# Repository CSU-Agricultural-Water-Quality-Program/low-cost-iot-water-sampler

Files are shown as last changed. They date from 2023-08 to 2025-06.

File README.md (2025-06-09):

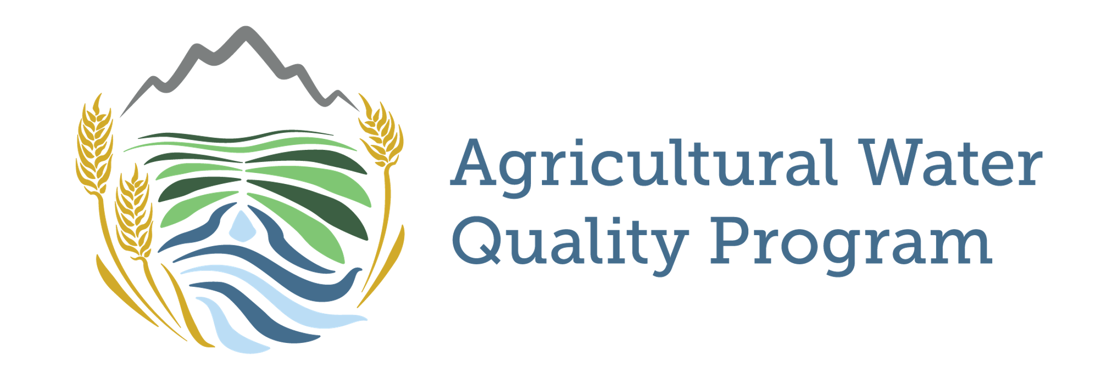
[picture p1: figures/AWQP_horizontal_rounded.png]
AWQP Logo (https://waterquality.colostate.edu)




# AWQP Low-Cost IoT Water Sampler
A low-cost, automated water sampler (LCS) with Internet of Things (IoT) technology for scalable, near-real-time water quality research developed by the Colorado State University Agricultural Water Quality Program (AWQP).

> [!NOTE]
> This project is actively under development. Code, parts, instructions, and other content are subject to change as we enhance the LCS. If you download/clone/fork this repository, we ask that you **please [email us directly](mailto:ansley.brown@colostate.edu;e.deleon@colostate.edu;erik.wardle@colostate.edu?subject=Inquiry%20about%20the%20Low%20Cost%20IoT%20Water%20Sampler%20from%20GitHub)** for the most up-to-date information and resources. We will also email you with any news related to the project moving forward!

## Table of Contents
- [Why create a low-cost water sampler?](#why-create-a-low-cost-water-sampler?)
- [Repo Contents](folder-contents)
- [Low Cost Sampler Description](#low-cost-sampler-description)
- [3D prints](#3D-prints)
- [Parts List](#parts-list)
- [How-to guide](#how-to-guide)
- [Known Bugs](#known-bugs)
- [Future Developments](#future-developments)
- [How to Cite](#how-to-cite)
- [License](#license)

---

## Why create a low-cost water sampler?
In Colorado and across the United States, agriculture is being identified as one source of nutrient
pollution in State and Federal waters. Nutrients such as nitrogen and phosphorus run off
farmlands and accumulate in surface waterways, causing water quality issues. Although
agricultural nonpoint sources are not currently regulated in Colorado, initiatives are set up to
encourage the adoption of Best Management Practices (BMPs) that protect surface water quality.
Quantifying BMP impacts on water quality, requires robust, edge-of-field (EoF) monitoring
systems that can accurately measure flow and collect water for nutrient and sediment analysis.
NRCS EoF standards currently require equipment that is often too costly for pragmatic and
scalable research. To address this need, the [Colorado State University Agricultural Water Quality
Program (AWQP)](https://waterquality.colostate.edu) has developed a low-cost, automated water sampler (LCS) with Internet of
Things (IoT) technology for scalable, near-real-time water quality research. This work directly
follows deliverables from an awarded NRCS Conservation Innovation Grant titled, “Next
Generation Technology for Monitoring Edge-of-Field Water Quality in Organic Agriculture”. The
CSU AWQP intends to create additional research and regulation opportunities for Colorado and beyond using this technology.

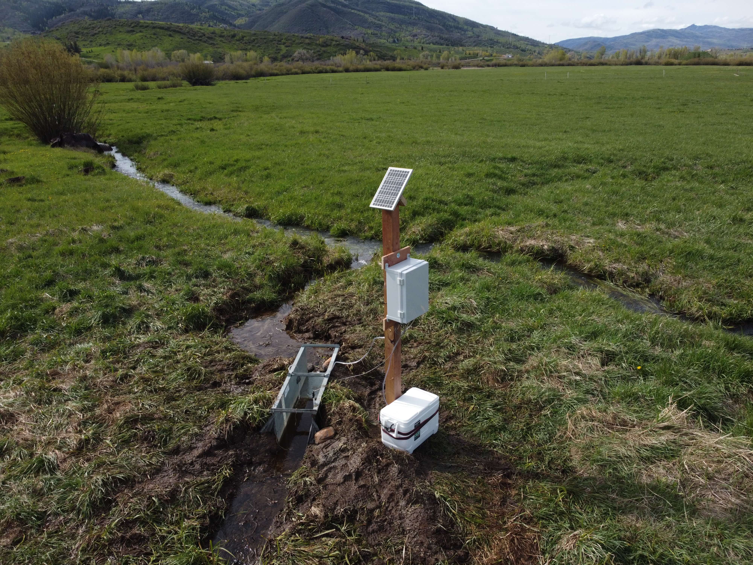
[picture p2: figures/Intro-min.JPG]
a deployed water sampler

**Figure 1.** Image of the low-cost automated water sampler (LCS) deployed at a mountain meadow hay field near Steamboat Springs, Colorado.

To learn more about AWQP, please visit [the AWQP website](https://waterquality.colostate.edu).

## Repo Contents
- .vscode
    - settings for flashing in VS code using the particle workbench add-on.
- compiled-firmwares
    - previously compiled firmwares for various borons (current code requires a unique binary for each device to accomodate for individual e-tape calibration)
- figures
    - figures embedded into README.md
- files
    - 3D prints: contains .STL files for printing that required for assembly
    - Bill of Materials: Excel with BOM, links, and prices 
- lib
    - libraries used in source code
- src
    - source code for particle boron flashing
    - config.h template for storing sensitive information like API keys and device-specific information needed to operate the LCS
- target
    - available firmware targets for particle devices
- .gitignore
    - files and folders to ignore when committing to the repository (e.g., config.h)
- AUTHORS.md
    - list of authors and contributors to the project
- CITATION.cff
    - citation file for the project, please use this to cite the LCS in your work
- CODE_OF_CONDUCT.md
    - code of conduct for the project, please read before contributing
- CONTRIBUTING.md
    - guidelines for contributing to the project, please read before contributing
- LICENSE.md
    - licensed under GNU General Public License Version 2 (GNU GPL V2.0)
- project.properties
    - contains project code and library dependencies
    
## Low Cost Sampler Description
The AWQP-developed LCS is comprised of five main components as shown in Figure 2: 1) device control panel 2) power assembly 3) pump assembly 4) a water depth sensor (eTape, MileOne), and 5) the water storage apparatus. 

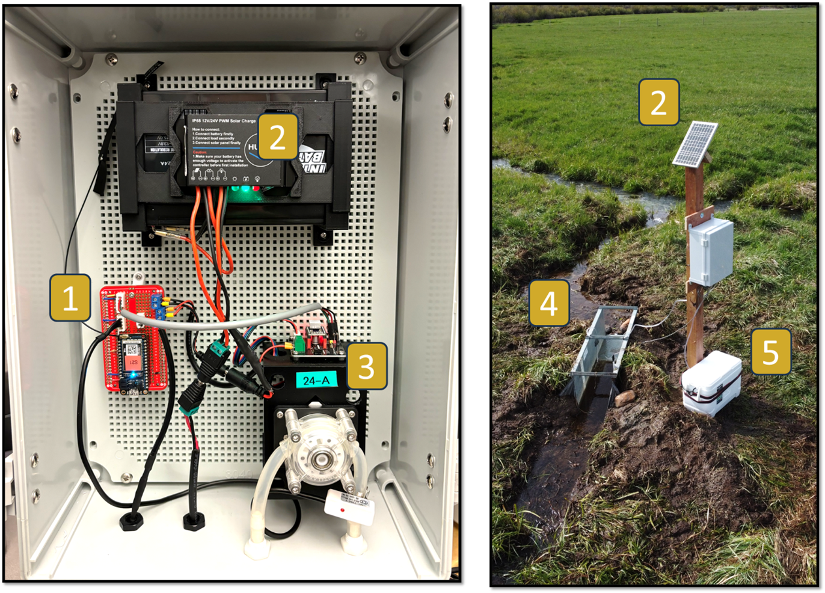
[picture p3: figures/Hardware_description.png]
low-cost sampler image

**Figure 2.** Picture of the low-cost automated water sampler (LCS) deployed in-situ, with its primary components annotated

Like commercial models, the LCS can detect and measure water flow in an installed flume via
depth, sample water at pre-determined or user-triggered intervals (in this case, hourly), preserve
water samples for later collection, remote data monitoring through cellular communications, and
stay powered remotely through solar and battery means. However, the LCS model accomplishes
this at approximately 1/10th of the cost of a commercial apparatus ($700-1,000). Additionally,
commercial models require the additional purchase of a cellular modem for wireless
connectivity, whereas the LCS integrally incorporates it into the microcontroller itself. Upon
completion of this experiment, the AWQP intends to open-source the LCS for future
collaborative development and sharing via GitHub repository on the AWQP GitHub
organization.

A preliminary comparison study performed by the AWQP indicate strong agreement between
LCS depth measurements and commercial bubbler units, with a root mean squared error (RMSE)
of 4.2 mm (n=1099). Additionally, measured analyte concentrations (total suspended solids,
NO3, NO2, Total N, Orthophosphate, Total Phosphorous) were similar, but lacked enough
sample points to accurately make a comparison. An example runoff depth measurement
comparison from an irrigation event at a corn field in Fort Collins, CO in 2020 is shown in
Figure 2.

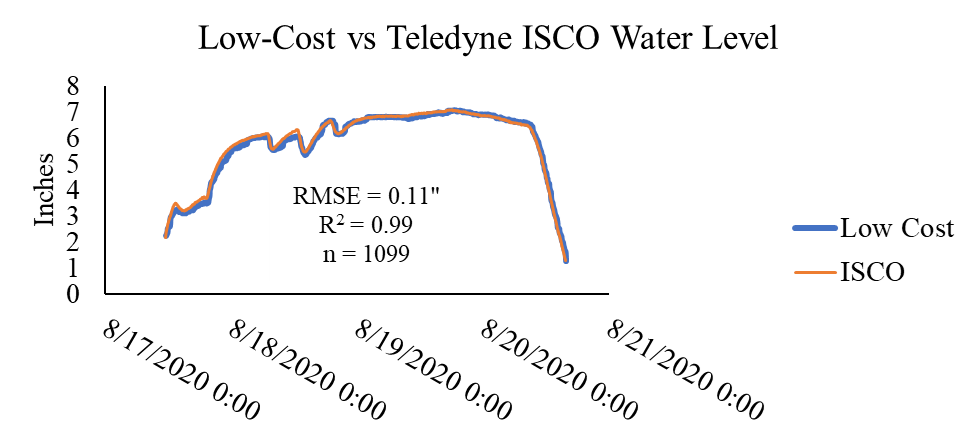
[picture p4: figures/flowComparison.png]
flow comparison graph

**Figure 3.** Results from a preliminary flow comparison study between the LCS and commercial Teledyne ISCO 6712 automated sampler.

## Software
- Particle Account and Particle Workbench on Virtual Studio Code is needed to claim a Particle Boron and flash calibration and sampler code.  
- Blynk IoT controls and monitors the LCS remotely via phone app. 
- (optional) Ubidots offers storage and visualization of sampler data. 

## 3D-prints
Can be found on our [AWQP Printables page](https://printables.com/@AgWaterQuality_66019):
* [Peristaltic pump mount](https://printables.com/model/560168-mount-for-a-peristaltic-pump)
* [12v Battery  mount](https://printables.com/model/560141-awqp-12v-battery-mount-for-the-low-cost-sampler)
* [Solar Controller Mount](https://www.printables.com/model/1177165-solar-controller-huine-mount-for-low-cost-iot-wate)
* [eTape TPU Cover](https://www.printables.com/model/1177200-milone-etape-tpu-protective-cover-for-awpq-low-cos) 

## Bill of Materials 
Please [contact the AWQP](mailto:ansley.brown@colostate.edu;e.deleon@colostate.edu;erik.wardle@colostate.edu?subject=Inquiry%20about%20the%20Low%20Cost%20IoT%20Water%20Sampler%20from%20GitHub) for the most current part list; these are often changing and being updated as improvements get implemented!

Current list updated 03 Jun. 2025:

[Bill of Materials](files/Bill%20of%20Materials.xlsx) 

## How-to guide
Introduction to major hardware components with a brief description:

- Enclosure: Protects the sampler components from the environment
- Pump Assembly: a peristaltic pump to collect water samples 
    - DRV8825 Motor Driver: Controls peristaltic pump with precision and efficiency
    - Non-contact water sensor: Detects water priming the pump
- Power Assembly: 12-volt Battery 
    - Solar Panel (10W): Charges Battery 
    - Solar Charging/Controller: Regulates power from the solar panel to the battery 
- Device Control Unit: PCB Carrier for the Particle Boron Microprocessor and all sensor connection points
- Water Depth Sensor: Using a eTape Water Level Sensor to monitor water level in flumes or streams. 
    - **Note:** For outdoors used  the sturdy eTape cable directly from the manufacturer, Milone Technologies.
- Water Storage Apparatus: Holds sample bottles and keeps collected samples cool. 

Brief Overview: 

1. Purchase all necessary hardware components (see [Bill of Materials](/files/Bill%20of%20Materials.xlsx))
2. 3D-print necessary mounting parts
3. Assemble hardware - [Here's our video guide!](https://youtu.be/WXuII_zaUJU?si=he2FRvl1eTsFYpLh)

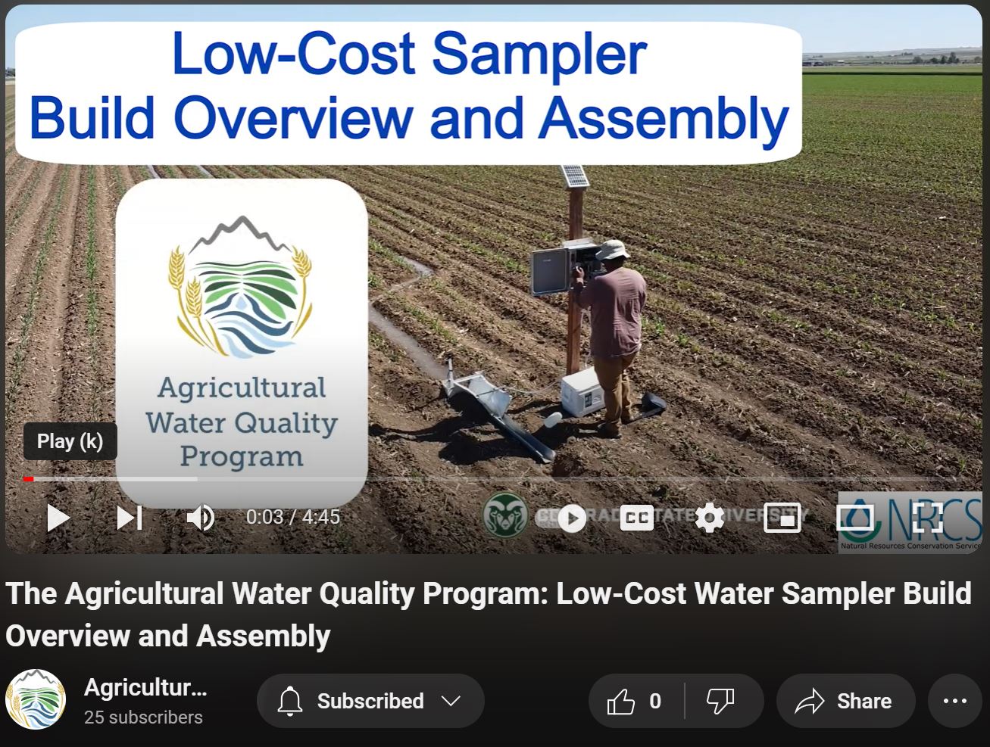
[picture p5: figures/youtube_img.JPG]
low cost sampler installation video (https://youtu.be/WXuII_zaUJU?si=he2FRvl1eTsFYpLh)


<br>  **Device Control Panel:** 

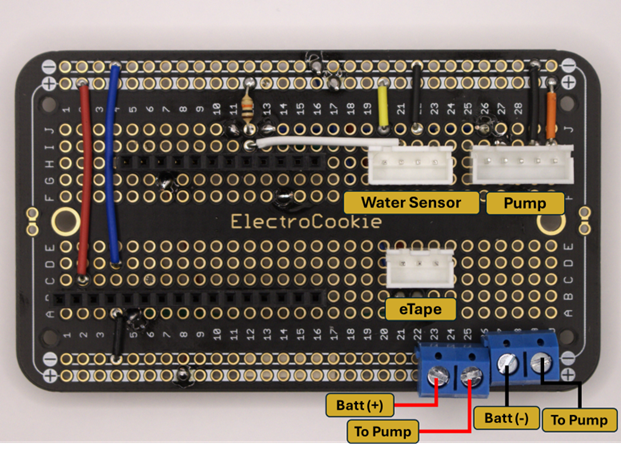
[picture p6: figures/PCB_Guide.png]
PCB Guide

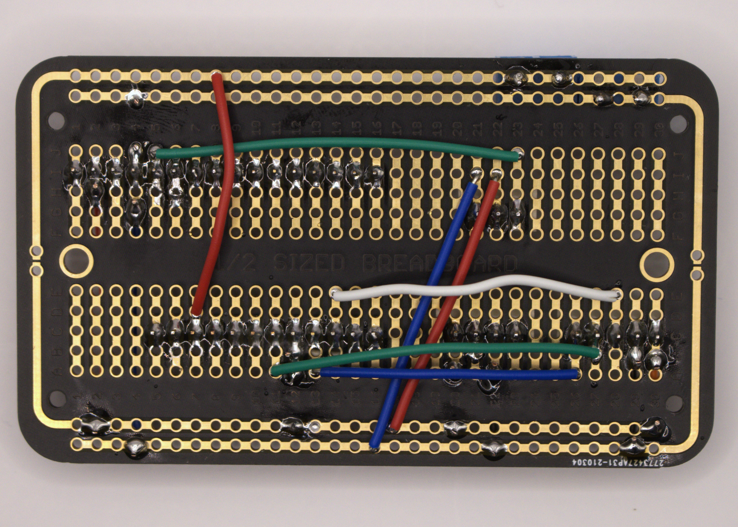
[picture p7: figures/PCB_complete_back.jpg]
    

**Figure 4.** Device Control Panel:  PCB front and back with wiring connection layouts and labels 

<br>

4. Make Blynk account and install Blynk phone application - [Bynk application website](https://blynk.io/)

The LCS requires user inputs to program the sampling protocol. These inputs include Volume to Sample (mL), Sampling Interval (min), Threshold (cm), Sample Bottle (mL). Using Blynk, users will input how much volume to collect (max 700mL per sample interval), how often to sample in minutes, the threshold depth in centimeters that will activate your sampler to start collecting water, and how large is the sample bottle to prevent sample slipovers.

- Setup Template 
- Add the following Datastreams as virtual pins 

<br>

| Name              | Virtual Pin | Data Type | Unit   | Min-Max    | Default |
|:-----------------:|:-------------:|:-----------:|:--------:|:------------:|:---------:|
| mL to Sample      | V1          | Integer   | (mL)   | 0 - 700   | 200     |
| Terminal Status   | V2          | String    |        |            |         |
| Sample Interval   | V3          | Integer   | (min)  | 0 - 720    | 60      |
| Threshold         | V4          | Integer   | (cm)   | 0 - 100    | 100     |
| Sample Bottle     | V5          | Integer   | (mL)   | 0 - 10000  | 2000    |
| Sample Now        | V9          | Integer   |        |            |         |
| mL to Collect     | V12         | Integer   | (mL)   | 0 - 1000   | na      |
| Current Threshold | V14         | Integer   | (cm)   | 0 - 100    | na      |
| Current Depth     | V17         | Integer   | (cm)   | 0 - 100    | na      |

<br>

5. (optional) Make Ubidots account - [Ubidots website](https://industrial.ubidots.com/)
6. eTape and Pump Calibration

    - eTape Calibration [Repo](https://github.com/CSU-Agricultural-Water-Quality-Program/AWQP-LCS-Etape-Calibration/tree/main) 
    - Pump Calibrtion [Repo](https://github.com/CSU-Agricultural-Water-Quality-Program/AWQP_LCS_pump_calibration)

7. Flash code from this repo, after updating the `config.h` file with your TOKENs from Blynk and Ubidots
8. Use the Blynk app to program your sampler 
9. Deploy and Enjoy!

### Configuration file instructions

For the code to run properly, you'll need to set up a `config.h` file with your API keys and other configurations.

1. **Navigate to the `src` directory**:
   - Inside the `src` directory, you will find a template file named `config_template.h`.

2. **Duplicate and Rename**:
   - Copy the `config_template.h` and rename the copied file to `config.h`.

3. **Add Your API tokens for Ubidots and Bylnk**:
   - Open `config.h` with a text editor of your choice. Replace the placeholders like `"YOUR_API_KEY_HERE"` with your actual API keys or other configuration details.

4. **Save and Close**:
   - After adding your details, save and close the file. Now your code should be able to run with your specific configurations.

> [!WARNING]
> Never commit your `config.h` with your actual API keys or Tokens to public repositories to ensure the privacy of your keys!

## Known bugs
- The water detection sensor is unreliable in its current state; we are not sure if this is a hardware or software issue at the moment. Currenlty working on fix. This does not affect the sampling process, but it does mean that the pump may not prime properly if the water detection sensor fails to detect water in the hose.
- In outdoor deployment, the normal wired Etape readings can bounce, leading to unintentional sampling. This bounce has not been observed in the strudier wired Etape specially requested with the TPU cover. We highly recommended to request the sturdy eTape cable directly from the manufacturer.
    - we tend to leave the trigger point at an unrealistically high number (e.g., 1000cm) until the device *should* be sampling, then we move it down to a realistic number (e.g., 2cm)
- Etape sensors only begin to accurately read depth at the 1" mark on the device
    - this is a hardware issue, and cannot be fixed in software
    - to circumvent this, we place the etape at -1" depths in the deployed stilling wells or other water bodies to ensure an accurate reading, then subtract 1" off of readings in post-processing for flow calculations.

## Latest updates
- v1.00 - Initial Release - Rough program outline with serial monitor// interface
- v1.01 - First Working Version, debugged with keyboard input of sample volume
- v1.02 - Uses Blynk  and WiFi for input and reporting instead of keyboard IDE
- v1.03 - Add stats and other Blynk features, provisions for prepurge of hose
- v1.04 - add a secound pump to the code
- v1.05 - coverted to particle using workbench
- v1.06 - added etape
- V1.07 - moved to new blynk IoT
- V1.08 - cleaned, added variable, add temp resistance to etapeand add project to private github repo
- V1.09 - added remote reset function
- V1.10 - added config.h file to store sensitive info and device speicific info
- V1.2 - fixed config.h file and updates bill of materials
- V1.21 - Added images, pinout, and blynk datastreams to the How To section
- V1.3 - Cleaned up code for Hardware X article release, commented out Ubidots code since it is optional, updated config.h file

## Future Developments
- Integrate a "time until next sampling" variable that can be called or sent at each payload
- make e-tape calibration coeficcients either a dictionary and/or a particle variable to alleviate the need for tailored binaries to flash each device.  Ultimately, this would allow users to make the device a particle product and enable fleet flashing.
- if the water detection sensor continues to fail we will add a "tube length" variable in the blynk app to calculate water needed to prime the pump prior to sampling.
- compare etape calibration data to see if a universal calibration equation can be developed for each etape length instead of having individual calibration equations for each device
- include firmware to add *in situ* water quality sensor like pH and turbidity 

## How to Cite

If you use the AWQP Low-Cost IoT Water Sampler (LCS) in your research or if it proves helpful in your work, please consider citing it. a [CITATION.cff](CITATION.cff) file is provided, or you can use the following BibTeX entry:

```bibtex
@misc{awqp_lcs_2025_v1p3,
  author       = {Emmanuel Deleon and Ansley Brown and Erik Wardle and Jakob Ladow},
  title        = {{Low-Cost IoT Water Sampler}},
  month        = jun,
  year         = 2025,
  note         = {Version 1.3},
  doi          = {10.5281/zenodo.15626855},
  publisher    = {Zenodo},
  url          = {https://zenodo.org/doi/10.5281/zenodo.15626855}
}
```

## License
This project is licensed under the GNU GENERAL PUBLIC LICENSE Version 2 (GNU GPL V2.0) - see the [LICENSE.md](LICENSE.md) file for details.

**Please visit [CSU STRATA's website](https://csustrata.org/technology-transfer/available-technology/low-cost-automated-water-sampler/) to inquire about a permissive commercial license for this project, and use the [contact form on that page](https://csustrata.org/technology-contact-2024-035/) for initiating that discussion.**

Copyright © 2023 Colorado State University Agricultural Water Quality Program. All rights reserved.

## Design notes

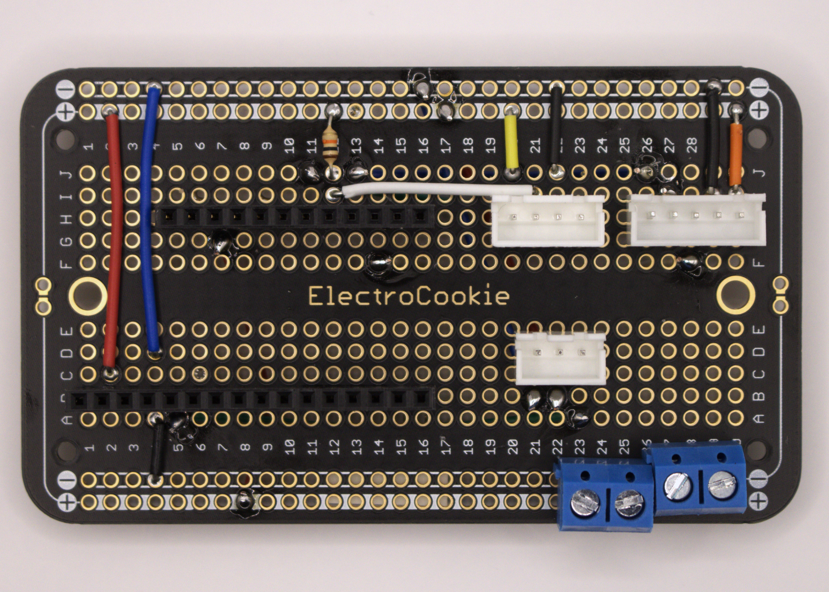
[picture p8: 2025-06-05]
figures/PCB_complete_front.jpg

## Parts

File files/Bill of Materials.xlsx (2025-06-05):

Designator | Component | Number | Cost per USD | Total cost USD | Source of materials | Material type
Waterproof Enclosure | Ogrmar ABS Plastic Dustproof Waterproof IP65 Junction Box Universal Enclosure with Lock (15.7"x11.8"x7") | 1 | $68.99 | $68.99 | Amazon (https://a.co/d/9mMv2tu) | Electronic Enclosure
Peristaltic Pump | INTLLAB High Flow Peristaltic Self-Priming Pump with Stepper Motor 12V/24V High Flow Peristaltic Pump, DP-520-48S | 1 | $45.80 | $45.80 | Amazon (https://www.amazon.com/gp/product/B082K6CYV1/ref=ppx_yo_dt_b_search_asin_title?ie=UTF8&th=1) | Non-specific
12 V Lead Acid Battery | ExpertPower 12V 7 Amp EXP1270 Rechargeable Lead Acid Battery | 1 | $22.76 | $22.76 | Amazon (https://www.amazon.com/ExpertPower-EXP1270-Rechargeable-Lead-Battery/dp/B003S1RQ2S) | Non-specific
Solar Panel | ECO-WORTHY 12V Solar Panel 10W Solar Panel | 1 | $23.99 | $23.99 | Amazon (https://www.amazon.com/dp/B00OZC3X1C?skipTwisterOG=1) | Non-specific
Solar Charge Controller | Huine 10A PWM Solar Charge Controller Waterproof IP68 12V 24V Solar Panel Controller Regulator | 1 | $19.99 | $19.99 | Amazon (https://www.amazon.com/HUINE-Waterproof-Controller-Intelligent-Regulator/dp/B07Q79TC2L) | Non-specific
Microcontroller | Boron LTE-M (NorAm) with EtherSIM (BRN404X) | 1 | $45.95 | $45.95 | Particle (https://store.particle.io/collections/cellular/products/boron-lte-cat-m1-noram-with-ethersim-4th-gen) | Non-specific
Breadboard PCB | ElectroCookie Prototype PCB Solderable Breadboard for Electronics Projects (5 Pack) | 1 | $8.06 | $8.06 | Amazon (https://www.amazon.com/gp/product/B07ZV8BKNF/ref=ppx_yo_dt_b_search_asin_title?ie=UTF8&psc=1) | Non-specific
Motherboard Standoffs | Motherboard Standoffs Plastic Mounting PCB | 1 | $8.99 | $8.99 | Amazon (https://a.co/d/34yRwN2) | Non-specific
DRV8825 Stepper Controller | HiLetgo 5pcs DRV8825 Stepper Motor Driver Module | 1 | $14.48 | $14.48 | Amazon (https://a.co/d/hqn6itl) | Non-specific
Stepper Controller Shield | Stepper Motor Driver Shield Expansion Board DRV8825/A4988 | 1 | $5.63 | $5.63 | Amazon (https://www.amazon.com/gp/product/B08RP2SCJ7/ref=ppx_yo_dt_b_search_asin_title?ie=UTF8&psc=1) | Non-specific
Female 16-Pin PCB Header Connector | 2.54mm Spacing Female 16 Pins PCB | 1 | $8.99 | $8.99 | Amazon (https://www.amazon.com/gp/product/B07HCCTY94/ref=ppx_yo_dt_b_search_asin_title?ie=UTF8&psc=1) | Non-specific
Female 12-Pin PCB Header Connector | 2.54mm Pitch 12 Terminals Straight Header | 1 | $6.99 | $6.99 | Amazon (https://www.amazon.com/gp/product/B07PVY4D52/ref=ppx_yo_dt_b_search_asin_title?ie=UTF8&psc=1) | Non-specific
PCB Terminal Pin | 2 Pin 3 Pin PCB Mount Screw Terminal Block Connectors Socket Strips 5.08mm | 1 | $5.98 | $5.98 | Amazon (https://www.amazon.com/gp/product/B0DPYF3M41/ref=ppx_yo_dt_b_search_asin_image?ie=UTF8&th=1) | Non-specific
Jumper wires | 24AWG 840 Pieces Jumper Wires Kit | 1 | $15.50 | $15.50 | Amazon (https://a.co/d/1k19Dlo) | Non-specific
eTape | 18" Standard eTape® Assembly with custom sturdy wiring (requires contacting customer service) | 1 | $65.00 | $65.00 | MiloneTech (https://milonetech.com/shop/ols/products/xn-standard-etape-assembly-75a-a8ed96/v/PN-12110215TC-AH-18) | Non-specific
Liquid Sensor | Non-Contact Water Level Sensor Capacitive Liquid Level Detector | 1 | $17.93 | $17.93 | Amazon (https://www.amazon.com/gp/product/B0832YDTPX/ref=ppx_yo_dt_b_search_asin_title?ie=UTF8&psc=1) | Non-specific
PG7 Glands | Cable Gland 20 Pack PG7 Waterproof | 1 | $8.99 | $8.99 | Amazon (https://www.amazon.com/gp/product/B09X4GK3FT/ref=ppx_yo_dt_b_search_asin_title?ie=UTF8&psc=1) | Polymer
Solar Barrel Jack Connectors | 12V Male + Female 2.1x5.5MM DC Power Jack Plug | 1 | $7.59 | $7.59 | Amazon (https://www.amazon.com/gp/product/B01J1WZENK/ref=ppx_yo_dt_b_search_asin_title?ie=UTF8&psc=1) | Non-specific
Load Barrel Jack Connectors | DC Power Pigtail Cable,5.5x2.1mm 18AWG Male and Female DC Connector Plug,12V 5A Barrel Jack (5 Pairs) | 1 | $6.66 | $6.66 | Amazon (https://www.amazon.com/Pigtail-5-5x2-1mm-Connector-Security-Lighting/dp/B0DB4N14F3?s=hi) | Non-specific
Dupont and JST Connector Kit | Taiss Dupont Crimping Tool Kit Ratcheting Wire Crimper with 2.54mm 600PCS Dupont Connectors and 560PCS JST XH Connectors, Dupont Crimper, JST Crimper(0.08-0.5mm² 28-20AWG) | 1 | $26.99 | $26.99 | Amazon (https://www.amazon.com/Taiss-Crimping-Ratcheting-Connectors-0-08-0-5mm%C2%B2/dp/B0C6PM9KGY?s=hi) | Non-specific
3-Pin Waterproof Connector | 3 Pin Electrical Connector 22AWG Waterproof IP65 Male Female Connector | 1 | $9.79 | $9.79 | Amazon (https://a.co/d/ewJF8lv) | Non-specific
Heat Shrink | 1/4" Heat Shrink Tubing - 3:1 Ratio Dual Wall Adhesive Lined | 1 | $9.99 | $9.99 | Amazon (https://a.co/d/8yxQi5g) | Non-specific
Cooler | Igloo BMX Hard Coolers (25qt) | 1 | $84.69 | $84.69 | Amazon (https://www.amazon.com/gp/product/B0B4X57WZY/ref=ppx_yo_dt_b_search_asin_title?ie=UTF8&psc=1) | Polymer
Tubing Adapter | 10 Packs 1/4 Thru-Bulk Bulkhead Plastic Hose Barb Fittings Plastic Hose Barb Fittings 1/4" | 2 | $8.89 | $8.89 | Amazon (https://www.amazon.com/dp/B0CBRNBYSD?ref=fed_asin_title) | Polymer
Sampler Tubing | PVC Tubing 1/4"ID X 3/8"OD Flexible Clear Vinyl Hose 100 Feet... | 1 | $29.89 | $29.89 | Amazon (https://www.amazon.com/gp/product/B07WCM9B9H/ref=ppx_yo_dt_b_search_asin_title?ie=UTF8&th=1) | Polymer
2 L Bottle | HDPE Bottles | 1 | $35.00 | $35.00 | Amazon (https://a.co/d/b2QJO2S) | Polymer
Hose Barb Fitting Elbow | Hose Barb Fitting Elbow 1/4" Hose Barb x 1/4" Male NPT Barbed Adapter for Fuel Gas Liquid Air | 1 | $11.98 | $11.98 | Amazon (https://a.co/d/fpFYtii) | Polymer
M3 x 12 mm Screws | M3 x 12mm 304 Stainless Steel | 1 | $6.92 | $6.92 | Amazon (https://a.co/d/5672PfI) | Metal
Solder & Seal Connectors | haisstronica 500PCS White Heat Shrink Butt Connectors 26-24 Gauge-Insulated Waterproof Electrical Butt Connectors | 1 | $29.39 | $29.39 | Amazon (https://a.co/d/eA2VKj1) | Polymer
Female Spade Connector | AIRIC Blue Female Spade Connector 16-14 AWG, 100 Pcs Nylon Electrical Crimps Terminal Connectors for Automotive Speaker Auto Stereo Wiring Connect Quick Disconnect Crimp Terminals for 16,14 Gauge Wire | 1 | $6.99 | $6.99 | Amazon (https://a.co/d/3NjjUDf) | Non-specific
M3 Nuts | Shapenty 100PCS 3mm Small Stainless Steel Female Thread Hex Screw Nut Fastener Tool, M3 | 1 | $5.99 | $5.99 | Amazon (https://a.co/d/iKg4BBT) | Metal
10K Resistor | 10K Ohm Carbon Film Single Fixed Resistor 1/2 W (0.5 Watts) 5% Tolerance, (10K R, 10K ohm, 10K Ω) Resistor (40 Pack) | 1 | $4.59 | $4.59 | Amazon (https://a.co/d/3N5jkZ8) | Non-specific
22 gauge 2 conductor wire | 22 Gauge Wire 2 Conductor Electrical Wire, 22 AWG Wire Stranded PVC Cord, 12V Low Voltage/Oxygen-Free Tinned Copper/Flexible 22/2 Wire for Automotive Marine LED Strips Lamps Lighting (30FT/ 9M) | 1 | $9.99 | $9.99 | Amazon (https://a.co/d/0057LE9) | Non-specific
XH2.54 to Dupont2.54 JST Connector Dupont Connector Kit | XH2.54 to Dupont2.54 JST Connector Dupont Connector Kit and Pre-Crimped 22AWG Cable, Compatible with JST-XH 2.54mm & Dupont 2.54mm 1/2/3/4/5/6/7/8/9/10Pin Housing 16cm Wire (XH-to-Dupont) | 1 | $19.99 | $19.99 | Amazon (https://a.co/d/ccCv97U) | Non-specific
22 Gauge 5 Conductor Electrical Wire | 22 Gauge 5 Conductor Electrical Wire, 16.4FT 22AWG Black PVC Stranded Tinned Copper 5 Wire Cable, 22/5 Extension Cable for LED Lamp Lighting, Automotive, Speaker, Access Control, etc. | 1 | $9.48 | $9.48 | Amazon (https://a.co/d/4QtEJwZ) | Non-specific
Electric Ferrule Crimping Tool Kit | FTK1200 Ferrule Crimping Tool Kit with Wire Crimper Tool, Secure Wire Ferrule Nylon Container, and 1,200 Electrical Wire Connectors, Electrician Tool Set for Home Improvement | 1 | $29.60 | $29.60 | Amazon (https://www.amazon.com/dp/B0CYTH8JSV) | Non-specific
PETG | 3D printing filament | 10 grams | $14.84 | $14.84 | Amazon (https://a.co/d/54kPzpl) | Polymer
TPU | 3D printing filament | 1 | $27.98 | $27.98 | Amazon (https://a.co/d/7lWdivt) | Polymer
 |  |  | Estimated Total | $791.24

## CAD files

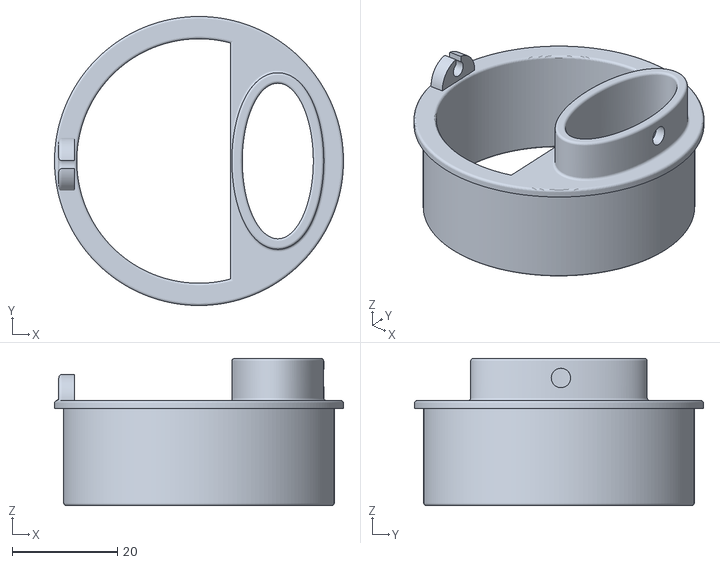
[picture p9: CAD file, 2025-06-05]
files/3D-prints/trap_flume_etape_and_PT_mount_STL.stl
55.0 x 55.0 x 28.0

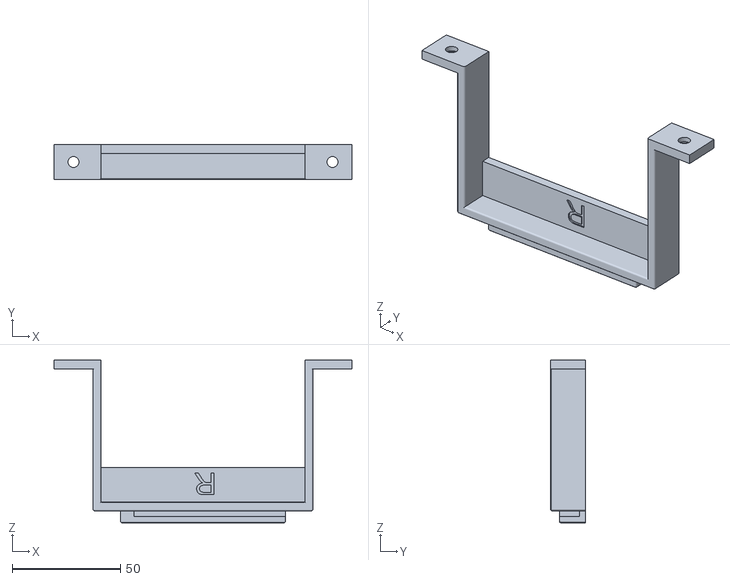
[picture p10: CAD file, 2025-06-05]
files/3D-prints/12Vbat_Umount_wSolarChargeHoles_Rightside.stl
137.5 x 16.0 x 75.0

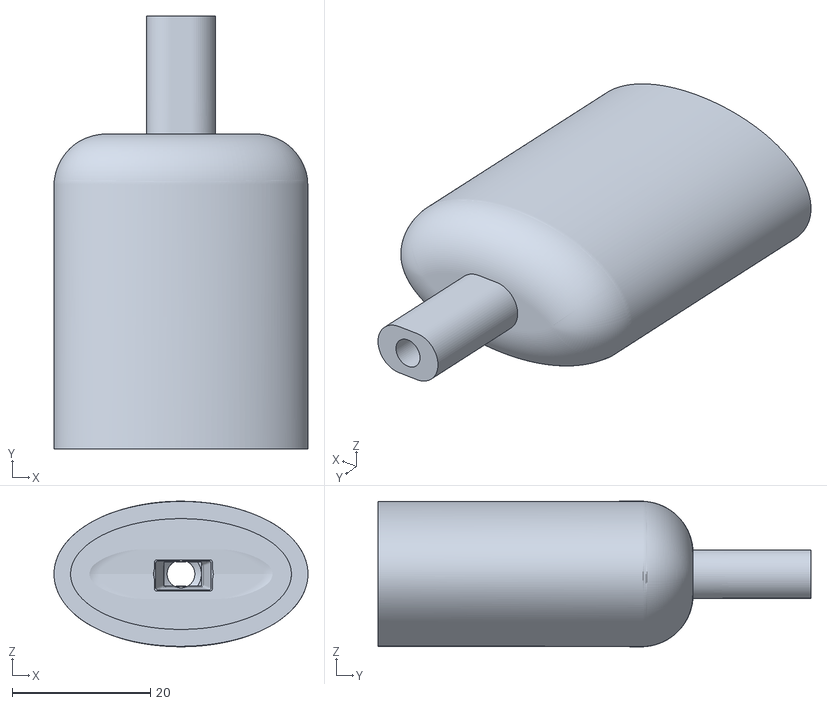
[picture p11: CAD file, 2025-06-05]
files/3D-prints/etapeTPUcover_STL.stl
36.7 x 62.5 x 21.0

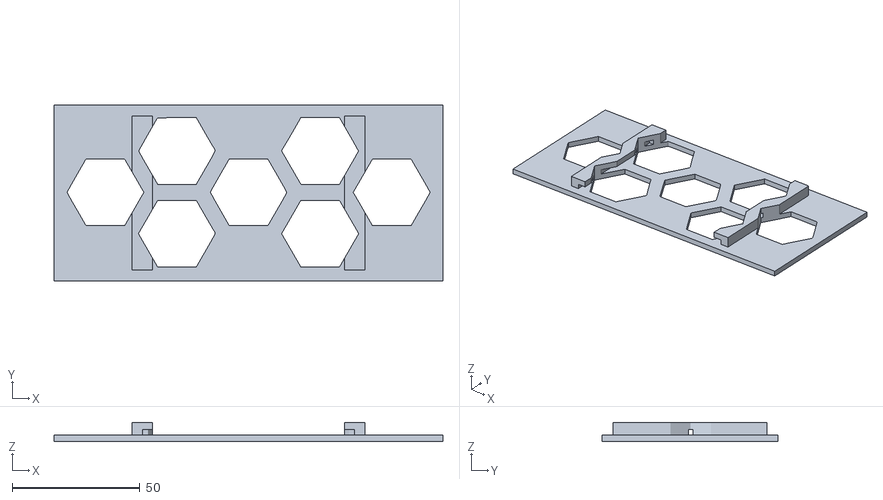
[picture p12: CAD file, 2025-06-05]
files/3D-prints/huine_solar_controller_mount.stl
152.0 x 68.6 x 7.50

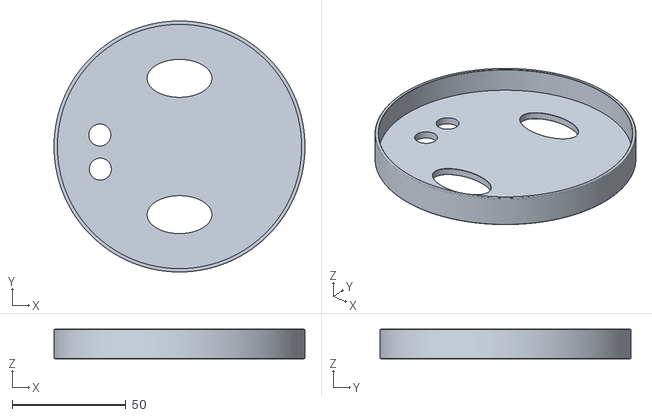
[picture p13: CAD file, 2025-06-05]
files/3D-prints/Etape_Calibration_cover Final.stl
110.5 x 110.5 x 13.0

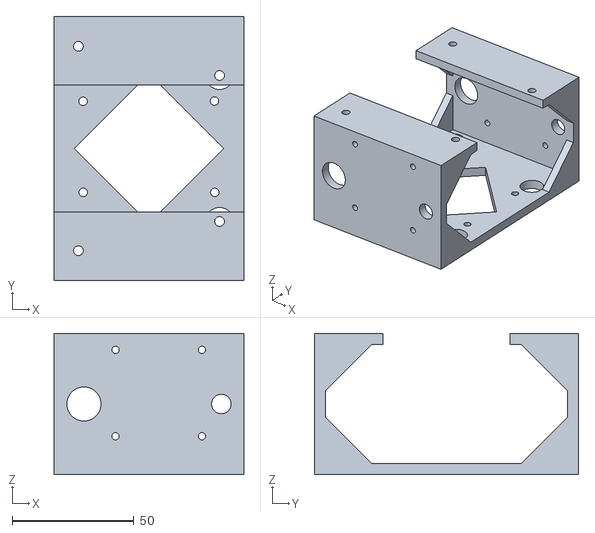
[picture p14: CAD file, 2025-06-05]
files/3D-prints/Sampler_Pump_Mount_STL.stl
78.0 x 108.5 x 58.0

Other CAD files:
files/3D-prints/12Vbat_Umount_wSolarChargeHoles_Leftside.stl
files/3D-prints/12v Battery mount_.f3d
files/3D-prints/huine_solar_controller_mount.f3d
files/3D-prints/trap_flume_etape_and_PT_mount v5.f3d

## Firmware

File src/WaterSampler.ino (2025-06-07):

/*
Project: Low-cost, IoT water sampler
Description: A low-cost, automated water sampler (LCS) with Internet of Things
 (IoT) technology for scalable, near-real-time water quality research developed
 by the Colorado State University Agricultural Water Quality Program.
 This version uses Blynk for control and user inputs.
 adapted from code written by chip mcclelland (seeinsight.com).
 Original Author: Emmanuel Deleon
Modified by: Dylan Casey, and A.J. Brown
Sponsor: Colorado State University Agricultural Water Quality Program
License: GNU GPL v2
Created Date: 27 Nov 2019
Last Update: 06 JUN 2025
Particle Boron Firmware Target: 6.2.1
*/

//#define SERIESRESISTOR 2000    //12-in. etape resistance
#define SERIESRESISTOR 2500    //15-in. etape resistance
//#define SERIESRESISTOR 3000    //18-in. etape resistance
//#define SERIESRESISTOR 4000    //24-in. etape resistance

#include "config.h" // include config file with tokens and other private info
#include <MeanFilterLib.h>  // setup library
#include <AccelStepper.h>
#include <QuickStats.h>
#include <Ubidots.h> 

// ######### Uncomment the following line if you want to use Ubidots ###########
Ubidots ubidots(UBIDOTS_TOKEN, UBI_TCP); // TOKEN from config.h file
// also uncomment lines 259 - 266 to use Ubidots
// #############################################################################


// ############################## Blynk Setup ##################################
// You should get Auth Token in the Blynk App.
// Go to the Project Settings (nut icon).
#define BLYNK_PRINT Serial  // setup blynk
#define BLYNK_DEVICE_NAME "Low Cost Water Sampler"
// Note that the Blynk Template ID is already defined in the config.h file
#include <blynk.h> // must be included after config.h and BLYNK_DEVICE_NAME
char auth[] = BLYNK_AUTH_TOKEN; // Blynk auth token from config.h file
// #############################################################################

// variable declarations
char depthString[16];               //   depth
char thresholdString[16];           //   threshold
char sample_numberString[16];       //   sample number
char sigString[16];                 //   signal strength


// state machine variables
enum State { INITIALIZATION_STATE, ERROR_STATE, IDLE_STATE, PRIME_STATE, SAMPLE_STATE, PURGE_STATE, REPORTING_STATE};
char stateNames[7][14] = {"Initialize", "Error", "Idle", "Priming", "Sampling", "Purging", "Reporting"};
State state = INITIALIZATION_STATE;
State oldState = INITIALIZATION_STATE;

// GPIO assignments
const int WATER_PIN = D4;    // pin for non contact water sensor, NPN
const int DIR_PIN1 = D3;  // Pump1 direction HIGH or LOW
const int STEP_PIN1 = D5;  // Pump1 start per step
const int STEPEN_PIN1 = D2; // Enables pump1 when LOW
const int VOLT_PIN = A2;     // read voltage source, 10:1 divider

byte sensorPin = A0;              // declaring etpae to particle 
int v = 0;                        // variable to store analog reading
int NUMSAMPLES=100;               // number of samples to take for data smoothing 
float measurements[100];          // variable for holding raw measurements
float smoothed;                   // variable for holding filtered measurement
float smoothedCV;  
float depth;
int Time_old;
float rssi = 0.00;

// Remote system reset variables
#define DELAY_BEFORE_REBOOT 2000
unsigned int rebootDelayMillis = DELAY_BEFORE_REBOOT;
unsigned long rebootSync = millis();
bool resetFlag = false;

// pump pulses required to purge lines
unsigned long currentMillis, startMillis, sampleMillis,purgeMillis;
unsigned long pulsetime, pulselast, pulseinterval; // timing variables
unsigned long primeMillis=0;
unsigned long maxprimeMillis=30*1000;   // max allowable pumping time to prime, e.g.30s
unsigned long maxsampleMillis=120*1000;   // max allowable sampling time to prime, e.g.120s
unsigned long maxpurgeMillis=60*1000;   // max allowable purging time , e.g.60s
unsigned long waterMean;    // avg of non contact water sensor

#define motorInterfaceType 1  // setup motor interface type
float volCal1 = 0.008259777;   // calculated millimeter per step
int ml_to_collect=0;  // example sample volume to collect
unsigned long sampleSteps = 5000; //set to number that if need to purge on system startup will purge that many steps in 3000 steps our pump will go 15 rotations
unsigned long sampleStepsPerge; 
unsigned long stepperSpeed = 1000; // Pump speed in steps per second
float battVolt;         // battery voltage

int sample_interval_min = 60;
unsigned long sample_interval_ms = 0;
unsigned long old_sample_millis = 0;
unsigned int sample_number = 1;
int threshold = 7;
int sample_bottle_mL = 4500;

boolean sample_now =false;

AccelStepper stepper1 = AccelStepper(motorInterfaceType, STEP_PIN1, DIR_PIN1);

MeanFilter<long> meanFilter(25);  // average non contact water sensor
MeanFilter<float>voltFilter(50);  // average non contact water sensor

QuickStats stats; //initialize an instance of this class


void setup() {
  
  Serial.begin(9600); // opens serial port, sets data rate to 9600 bps
    // connect to blynk
  //Particle.keepAlive(PARTICLE_KEEPALIVE);
  delay(2000);
  Blynk.begin(auth);
  Blynk.virtualWrite(V2, "clr");  // clear Terminal Widget
  Blynk.virtualWrite(V2, "4G connected! Sampler Active!\n");
  Blynk.syncVirtual(V1);  // sync slider value

  while (!Serial) {
    ; // wait for serial port to connect. Needed for native USB
  }
  Serial.setTimeout(10);
  pinMode(LED_BUILTIN, OUTPUT);
  pinMode(STEP_PIN1, OUTPUT);
  pinMode(DIR_PIN1, OUTPUT);
  pinMode(STEPEN_PIN1, OUTPUT);
  
  pinMode(WATER_PIN, INPUT_PULLUP);  // water detector

  stepper1.setMaxSpeed(1200); // Set the maximum speed in steps per second:
  
  for (int x = 0; x < 40; x++) {  // read non contact water sensor on hose
    waterMean = meanFilter.AddValue(digitalRead(WATER_PIN)); 
  }
    state = PURGE_STATE;

  digitalWrite(STEPEN_PIN1, LOW); // Pump1 on
  
  sample_interval_ms = sample_interval_min * 60 * 1000;

// Particle variables for Particle app
Particle.variable("depth", depthString); 
Particle.variable("threshold", thresholdString);
Particle.variable("next_sample_number", sample_numberString);
Particle.variable("signal", sigString);

//  Remote Reset Function Setup
Particle.function("reset", cloudResetFunction);
    
}  // end setup

void loop() {
  Blynk.run();
  switch(state) { // state machine  starts here
  
  case IDLE_STATE:
   if (state != oldState) printStateTransition();
   if (ml_to_collect>0 && check_sample_interval()==1 && depth >= threshold && check_sample_number()==1) state = PRIME_STATE;
   else if (ml_to_collect>0 && sample_now) state = PRIME_STATE;
   break;

  case PRIME_STATE:
    if (state != oldState) printStateTransition();
    if (!primeSystem())
    {
      state = ERROR_STATE;
     }
    else state = SAMPLE_STATE;
  break;

  case SAMPLE_STATE:
    if (state != oldState) printStateTransition();
    if (!collectSample())
    {
      state = ERROR_STATE;
    }
    else state = PURGE_STATE;
    
    Blynk.virtualWrite(V2, sample_number);
  
  break;

 case PURGE_STATE:
   if (state != oldState) printStateTransition();
   if (!purgeSystem())
    {
      state = ERROR_STATE;
    }
    else 
    state = REPORTING_STATE;
   break;
  
 case REPORTING_STATE:
   if (state != oldState) printStateTransition();
   if (!reportingData())
   {
     state = ERROR_STATE;
   }
   else 
   {
    //ml_to_collect=0;
    sample_now=false;
    state = IDLE_STATE;
   }
 break; 
 
 case ERROR_STATE:                                                   // To be enhanced - where we deal with errors
    if (state != oldState) printStateTransition();
    //Serial.println("Halted in error state");
    Blynk.virtualWrite(V2, "Halted in error state\n");
    while(1);  // halt
 break;
  
 } // end switch

// take reading every 5 min
if(Time.minute() % 5 == 0 && Time_old != Time.minute()){ //read every 20 min. change the "10" to change sample interval in min (1 - 59)

//Collect etape measurments:
  for(int i=0;i<NUMSAMPLES;i++){
    v=analogRead(sensorPin);
    measurements[i]=(v); // convert to volts
    delay(10);  // Change (or remove) this delay value to alter the sampling time span.
  }  
  smoothed = stats.median(measurements,NUMSAMPLES); // Median filter (choose which filter to use)
  //smoothed=stats.average(measurements,NUMSAMPLES); // Mean filter 
  //smoothedCV=stats.CV(measurements,NUMSAMPLES); // CV of readings  
  smoothed = (4095 / smoothed) - 1; // convert to resistance
  smoothed = SERIESRESISTOR / smoothed; // convert to voltage
  
/* Convert voltage to depth based on custom etape linear calibration curve
   etape product link: https://milonetech.com/products/standard-etape
   etape data sheet: https://img1.wsimg.com/blobby/go/6e1bce17-f4fa-40c3-9d89-9bb7445697bb/downloads/Standard%20eTape%20Data%20Sheet.pdf 
  
   Use the following equation as per the mileone etape manual guidelines
     depth = (A*smoothed) + B
     where A = (depth_2-depth_1)/(resistance_2-resistance_1) and B = depth_1 - A*resistance_1
   or where multiple resistances are plotted against depth and fitted with an OLS regression line
     depth = (slope*smoothed) + intercept
*/
 depth = (-0.01695*smoothed) + 46.2695; // current selected calibration
 //depth = (-0.01686*smoothed) + 46.99; // comment other curves for convenience to use on other sampler units


  snprintf(depthString,sizeof(depthString) -1, "%4.1f cm", depth);  // convert to string

  CellularSignal sig = Cellular.RSSI(); // get signal strength
  rssi = sig.getQuality(); // get signal quality
  float strength = sig.getStrength();
  snprintf(sigString,sizeof(sigString), "%.02f %", strength);
 
  /* 
  //################## Uncomment to use Ubidots ###############################
  ubidots.add("Level_cm", depth);  // send data to ubidots
  //ubidots.add("Volts", voltage);
  //ubidots.add("SoC", SoC);
  //ubidots.add("Rssi", rssi);
  ubidots.add("SigS", strength);
 
    bool bufferSent = false;
    bufferSent = ubidots.send();  //Send data to ubidots
  //###########################################################################
  */ 
    Time_old = Time.minute(); // resetting time 
  }

// Remote Reset Function
if ((resetFlag) && (millis() - rebootSync >=  rebootDelayMillis)) {
    // do things here before reset if necessary and then push the button
    Particle.publish("Debug", "Remote Reset Initiated", 300, PRIVATE);
    System.reset();
  }

} // end main loop

bool primeSystem() {    // prime system with water 
   //digitalWrite(DIR_PIN, HIGH);  // Pump forward
   digitalWrite(STEPEN_PIN1, LOW); // Pump on

   startMillis=millis();
   currentMillis=startMillis;
   waterMean = meanFilter.AddValue(digitalRead(WATER_PIN)); //  noncontact water sensor on hose
   while (waterMean != 0 && (currentMillis-startMillis)<maxprimeMillis){
     stepper1.setSpeed(stepperSpeed);
     stepper1.runSpeed();
     currentMillis=millis();   // wait for prime of tubing or runs of time
     waterMean = meanFilter.AddValue(digitalRead(WATER_PIN)); //  noncontact water sensor on hose
     Blynk.run();
   }
   stepper1.stop();       // turn Pump1 Off
   delay(50);
   if((currentMillis-startMillis)<=maxprimeMillis){
    primeMillis=currentMillis-startMillis;
   //Serial.print("Prime time: ");  Serial.println(primeMillis/1000);
    return 1;   // successful prime
   }
   else return 0;   // prime failed
   
}
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

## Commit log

2023-08-21 Initialized repo with most current code
    Manny gave AJ a LCS code on 21 Aug 2023. That is initialized here. AJ deleted previous git attributes and README.md files.
2024-04-15 Update README.md
    updated readme with current CSU STRATA webpage for LCS
2024-07-09 added stls and bill of materials
    [12Vbat_Umount_wSolarChargeHoles_leftside.stl, 12Vbat_Umount_wSolarChargeHoles_rightside.stl, Bill of Materials.xlsx, INTLLAB Stepper 12V24V High Flow Peristalt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]
2025-02-06 added calibration folders
2025-02-06 Added pump calibration files
2025-03-05 removed calibration files and fixed up readme
    [12Vbat_Umount_wSolarChargeHoles_leftside.stl, 12Vbat_Umount_wSolarChargeHoles_rightside.stl, INTLLAB Stepper 12V24V High Flow Peristaltic Pump, DP-520-48S.stl]
2025-05-08 added 3d files
    [12Vbat_Umount_wSolarChargeHoles_Leftside.stl, 12Vbat_Umount_wSolarChargeHoles_Rightside.stl, 12v Battery mount_.f3d, Bill of Materials.xlsx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]
2025-05-24 added calibration repo links
2025-06-04 Updated BOM
    [Bill of Materials.xlsx]
